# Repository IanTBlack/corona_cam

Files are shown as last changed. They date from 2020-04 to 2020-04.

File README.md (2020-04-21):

# Corona Cam
[The original In-situ Plankton Assemblage eXplorer (IPAX) was developed by Pichaya Lertvilai at UCSD](https://agu.confex.com/agu/osm20/meetingapp.cgi/Paper/648464). The Corona Cam is an attempt at recreating the IPAX that was presented at Ocean Sciences Meeting 2020.

Pichaya has set up a repo for the IPAX here: https://github.com/plertvilai/IPAX  

Similar to the IPAX, the Corona Cam seeks to provide a low cost method (~400 USD) for in-situ photography and video recording of very tiny things in the ocean (50-200 microns), such as zooplankton.

**Specs**

**Sensor Type: Sony IMX219 8MP**

**Lens: 1/2.5" 4mm M12 (swappable)**

**Brains: Raspberry Pi Zero W**

**LEDs: Adafruit NeoPixel Ring - 16x RGBW Cool White**

**Case: Blue Robotics 3" Watertight Enclosure (rated for 100m depth)**

**Battery: 5V rechargeable lithium-ion (i.e. cell phone power pack)**

**Video Resolution, Framerate, Format: 1920x1080, 30, .h264**

**Still Image Resolution: 3280x2464**  

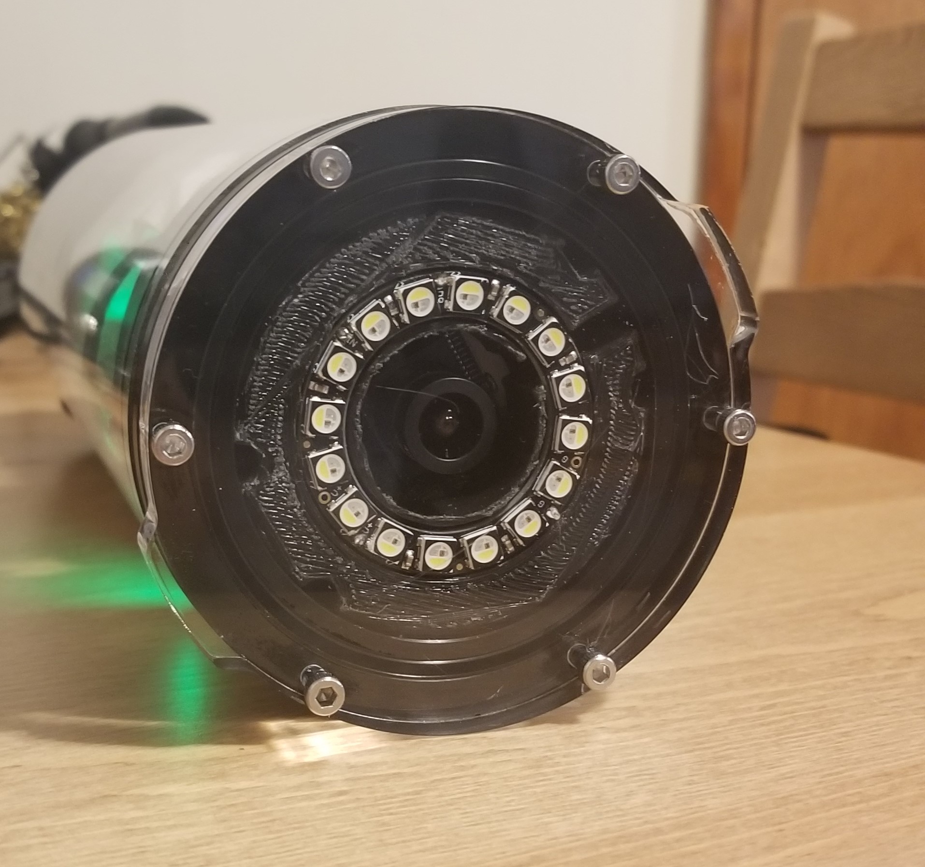
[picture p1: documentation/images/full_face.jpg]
Face


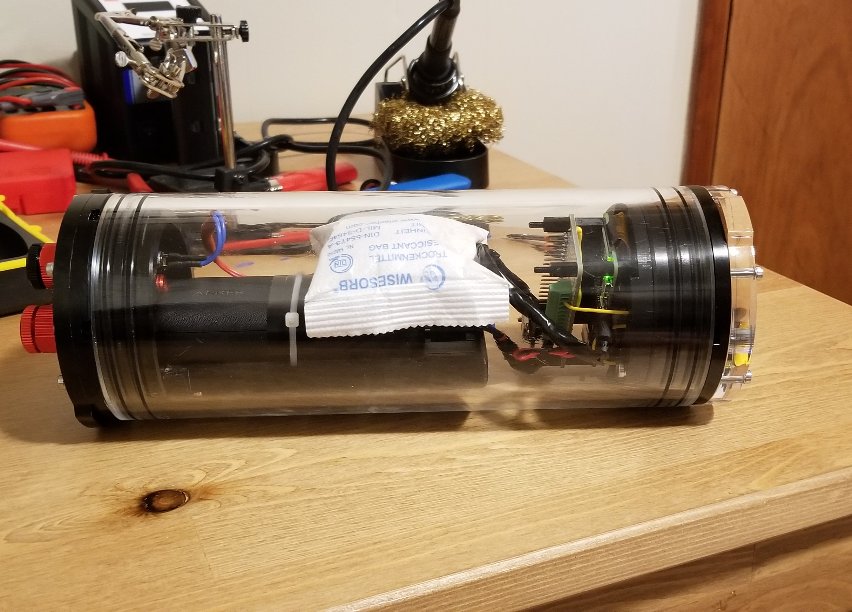
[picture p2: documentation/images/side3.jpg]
Side


The Corona Cam took approximately 9 pots of coffee and 72 Coronas to develop.

## Operation
The camera utilizes cron to operate at user-defined times. This allows the camera to operate at intervals or at specific times. The length of the recording, the recording format, and LEDs are controlled by the Python script that is run through cron.

## Repository Structure
### 3d_prints
This folder contains .ipt, .stl, and .gcode files for the camera mount, battery mount, and camera setup tool. For the .gcode files, Ultimaker Cura 4.5 was used as the slicer for printing on an Ender 5 Pro. The readme.txt file in that folder details the settings used. All three parts require approximately 300g of PLA and ~21 hours of print time.

### documentation
This folder contains drawings, guides, and manuals that were used in the development of the Corona Cam. It is recommended that you review this material if you run into any issues.
A build list is also provided. The primary vendors in this build list are Adafruit, Amazon, Blue Robotics, DLS Corp, and M12 Lenses. Note that the total price listed in the build list only considers the primary parts and does not consider 3D printing costs, consumables, tools, or other peripheral electronics (monitor, keyboard, mouse).

### scripts
This folder contains scripts for testing build components, a script that assists with setting up the Pi, and scripts that are run under crontab.

## Contact
For questions and comments, contact: Ian Black (blackia@oregonstate.edu)

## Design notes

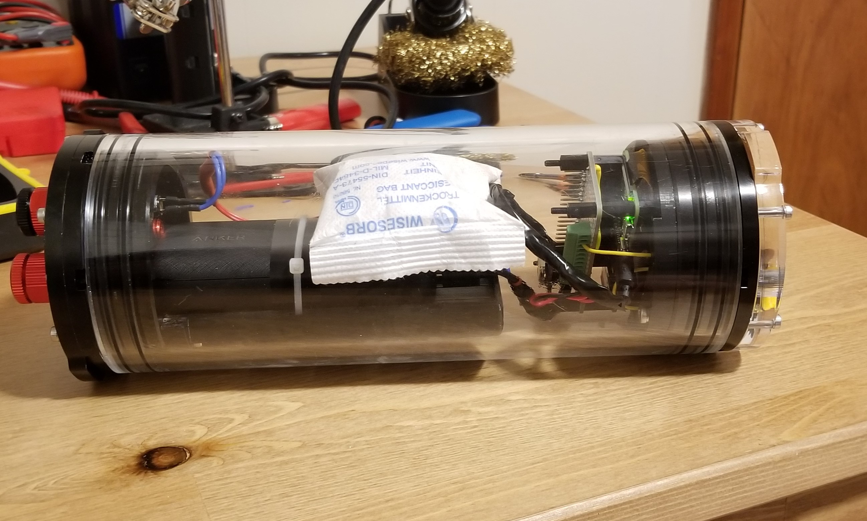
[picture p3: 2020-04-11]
documentation/images/side2.jpg

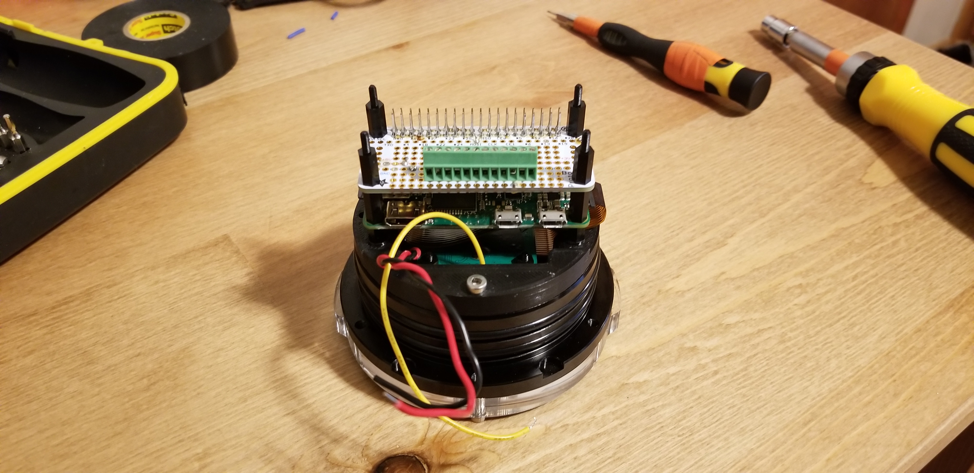
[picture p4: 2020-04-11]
documentation/images/cam_proto.jpg

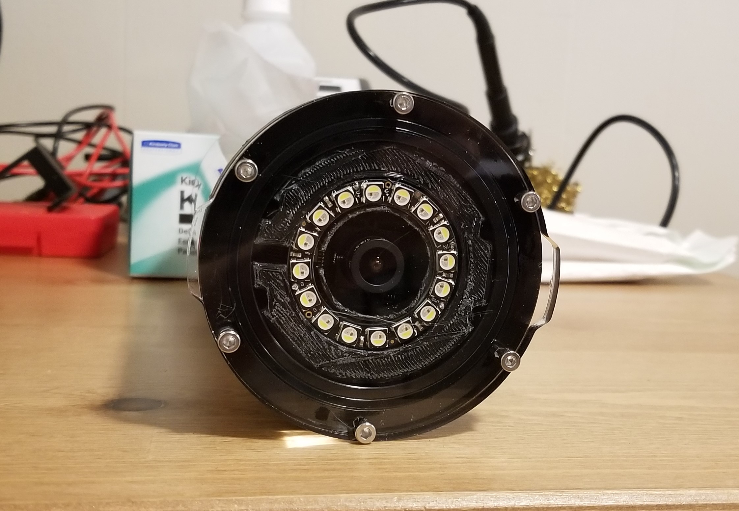
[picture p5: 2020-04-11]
documentation/images/cam_1.jpg

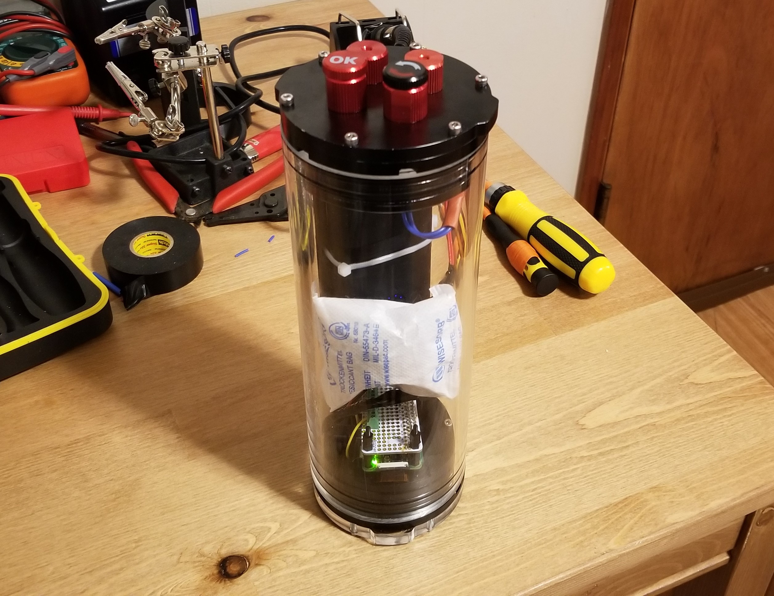
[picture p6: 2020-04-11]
documentation/images/tall.jpg

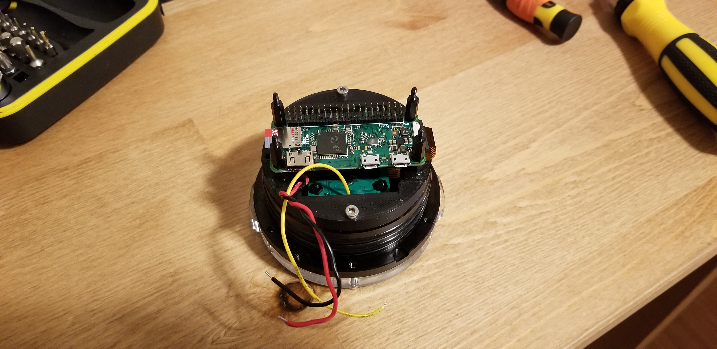
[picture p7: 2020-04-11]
documentation/images/pi_standoffs.jpg

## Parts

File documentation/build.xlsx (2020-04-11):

Total (Build) | 371.40
Part | Vendor | Part ID | Price Per Unit | Units | Subtotal | Comment | Check
Build
Raspberry Pi Zero W (https://www.adafruit.com/product/3400) | Adafruit | 3400 | 10.00 | 1 | 10.00 | Brains of the camera.
NeoPixel Ring - 16 RGBW (https://www.adafruit.com/product/2856) | Adafruit | 2856 | 11.95 | 1 | 11.95 | Lights for the camera.
Adafruit Perma Proto Bonnet Mini Kit (https://www.adafruit.com/product/3203) | Adafruit | 3203 | 4.50 | 1 | 4.50 | For connecting the NeoPixel/peripherals.
Raspberry Pi Zero v1.3 Camera Cable (https://www.adafruit.com/product/3157) | Adafruit | 3157 | 5.95 | 1 | 5.95 | For connecting the camera to the RPi.
Stacking Header for Pi - Extra Tall (https://www.adafruit.com/product/1979) | Adafruit | 1979 | 2.95 | 2 | 5.90 | For connecting the Protoboard to the Pi.
Adafruit PiRTC - DS3231 (https://www.adafruit.com/product/4282) | Adafruit | 4282 | 14.95 | 1 | 14.95 | For keeping time.
8-Pin Terminal Block (https://www.adafruit.com/product/2141) | Adafruit | 2141 | 2.75 | 1 | 2.75 | For connecting NeoPixel to protoboard.
Nylon Hex Standoffs - M2.5 (https://www.amazon.com/gp/product/B06XKWDSPT/ref=ppx_yo_dt_b_asin_title_o01_s00?ie=UTF8&psc=1) | Amazon | NLLZLM320PM25 | 12.99 | 1 | 12.99 | For connecting camera and RPi components to 3D printed camera mount.
CR1220 Coin Cell (https://www.amazon.com/Energizer-Lithium-Watch-Mercury-Batteries/dp/B00N9HRAAO) | Amazon | B00N9HRAAO | 5.49 | 1 | 5.49 | For powering PiRTC.
Breakaway Headers (https://www.adafruit.com/product/392) | Adafruit | 392 | 4.95 | 1 | 4.95 | Soldered to Pi.
3" Flange (https://bluerobotics.com/store/watertight-enclosures/3-series/o-ring-flange-3-series/) | Blue Robotics | WTE3-M-FLANGE-SEAL-R2-RP | 24.00 | 2 | 48.00 | Dual o-ring seal against the tube.
3" Aluminum End Cap - 4 Holes (https://bluerobotics.com/store/watertight-enclosures/3-series/wte3-m-end-cap-4-hole-r1/) | Blue Robotics | WTE3-M-END-CAP-4-HOLE-R1-RP | 12.00 | 1 | 12.00 | Single o-ring seal against the flange
3" Acrylic End Cap (https://bluerobotics.com/store/watertight-enclosures/3-series/wte3-p-end-cap-r1/) | Blue Robotics | WTE3-P-END-CAP-R1-RP | 10.00 | 1 | 10.00 | Single o-ring seal against the flange
3" Acrylic Tube - 8.75" (https://bluerobotics.com/store/watertight-enclosures/3-series/wte3-p-tube-8p75-r1/) | Blue Robotics | WTE3-P-TUBE-8P75-R1-RP | 35.00 | 1 | 35.00 | Main body of the camera.
Switch (https://bluerobotics.com/store/comm-control-power/switch/switch-10-5a-r1/) | Blue Robotics | SWITCH-10-5A-R1-RP | 15.00 | 1 | 15.00 | For turning the camera on and off.
Enclosure Vent Plug (https://bluerobotics.com/store/cables-connectors/penetrators/vent-asm-r1/) | Blue Robotics | VENT-ASM-R3-RP | 9.00 | 1 | 9.00 | For venting the camera.
M10 Blank Penetrator (https://bluerobotics.com/store/cables-connectors/penetrators/penetrator-blank-10-25-a-r2/) | Blue Robotics | PENETRATOR-M-BLANK-10-25-R3-RP | 4.00 | 2 | 8.00 | Placeholder for other sensors.
IMX219 - 8.0 MP Camera With M12 Mount (https://dlscorp.com/shop/imx219-8-0-mp-raspberry-pi-compatible-camera-module/) | DLS Corp | B0152 | 69.99 | 1 | 69.99 | Choose M12 Metal Mount - 16.5mm, No IR Filter
M12 1/2.5" 4mm Lens (http://www.m12lenses.com/4-0mm-F2-0-5MP-M12-Mount-CCTV-Lens-p/pt-0420cw-5mp.htm) | M12 Lenses | PT-0420CW-5MP | 17.00 | 1 | 17.00 | For taking video of tiny things.
microSD card - 128GB (https://www.amazon.com/Samsung-MicroSDXC-Adapter-MB-ME128GA-AM/dp/B06XWZWYVP) | Amazon | B06XWZWYVP | 21.99 | 1 | 21.99
Anker 10000mAh Power Pack (https://www.amazon.com/Anker-PowerCore-10000mAh-Portable-Delivery/dp/B07PXMF52C) | Amazon | B07PXMF52C | 33.99 | 1 | 33.99 | For powering the pi.
Right Angle microUSB Cable (https://www.amazon.com/s?k=microUSB+right+angle&ref=nb_sb_noss_2) | Amazon |  | 12.00 | 1 | 12.00 | Right angle allows for clearance to the case. An upward one might allow for connection to the PWR microUSB port, otherwise, use of the USB USB port is okay.
Consumables
Spare O-Rings (https://bluerobotics.com/store/watertight-enclosures/3-series/wte3-o-ring-set-r1/) | Blue Robotics | WTE3-O-RING-SET-R1-RP | 3.00 | 2 |  | You never know.
316SS M3 Hardware (Extra - 10mm long) | Blue Robotics | By Request |  |  |  | Extras for connecting 3D prints to flanges.
22 AWG Wire |  |  |  |  |  | Really just need three colors (V+,GND,signal).
AA Batteries (https://www.amazon.com/Energizer-Batteries-Battery-Alkaline-E91BP-24/dp/B004U429AQ) |  |  |  |  |  | For powering the camera.
Rosin Core Solder (https://www.amazon.com/Kester-solder-Rosin-Core-Spool/dp/B001W2XZOS) |  |  |  |  |  | For soldering wires.
Heatshrink
Tools
Penetrator Wrench (https://bluerobotics.com/store/cables-connectors/tools/tool-penetrator-wrench-r1/) | Blue Robotics | TOOL-PENETRATOR-WRENCH-R1-RP | 13.99 | 1 or 2 |  | Not necessary, but prevents marring of the aluminum during installation. Exposed aluminum will corrode when exposed to seawater for long periods of time.
Soldering Iron (https://www.amazon.com/gp/product/B00EO4CUHY/ref=ppx_yo_dt_b_search_asin_title?ie=UTF8&psc=1) |  |  |  |  |  | The XYTronic 258 will do what you need it to do. Nothing fancy.
Wire Strippers (https://www.amazon.com/Stripper-Stranded-Klein-Tools-11057/dp/B000XEUPMQ) |  |  |  |  |  | Just need to be able to strip 22 AWG.
Forceps |  |  |  |  |  | Helps when forming solder joints.
Flush Cutters |  |  |  |  |  | Helps when trimming pins and solder joints.
Third Hand
Electronics
Powered USB 2.0 Hub (https://www.amazon.com/gp/product/B07W3M16C1/ref=ppx_yo_dt_b_asin_title_o00_s00?ie=UTF8&psc=1) | Amazon | B07W3M16C1 | 17.99 | 1 |  | The Pi Zero can be tricky when hooking up peripherals. It only likes USB 2.0 and it can't really supply enough power for peripherals like a keyboard and mouse, so a separately powered USB 2.0 hub is required.
Mini-HDMI to HDMI (https://www.amazon.com/gp/product/B014I8UAPE/ref=ppx_yo_dt_b_asin_title_o02_s00?ie=UTF8&th=1) | Amazon | B014I8UAPE | 6.45 | 1 |  | RPi Zero to monitor.
Micro-USB to USB (https://www.amazon.com/gp/product/B00LN3LQKQ/ref=ppx_yo_dt_b_asin_title_o02_s00?ie=UTF8&psc=1) | Amazon | B00LN3LQKQ | 4.99 | 1 |  | Rpi Zero to powered USB 2.0 Hub to keyboard and mouse.
Monitor |  |  |  |  |  | Helps with initial set up , unless you are SSH savvy.
Keyboard
Mouse

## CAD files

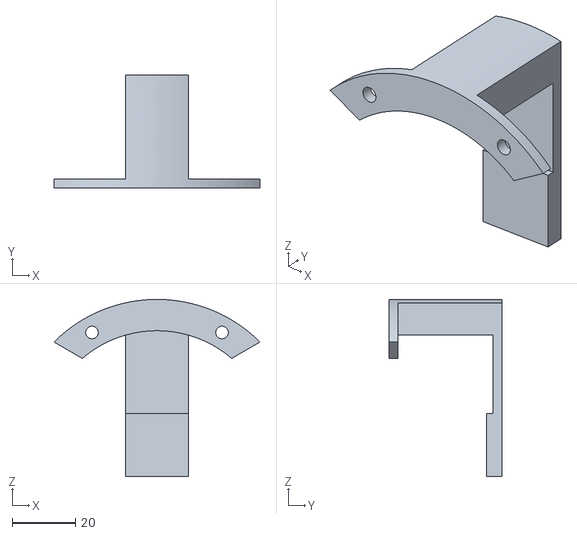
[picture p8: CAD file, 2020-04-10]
3d_prints/stl/corona_setup_tool.stl
65.4 x 36.0 x 56.2

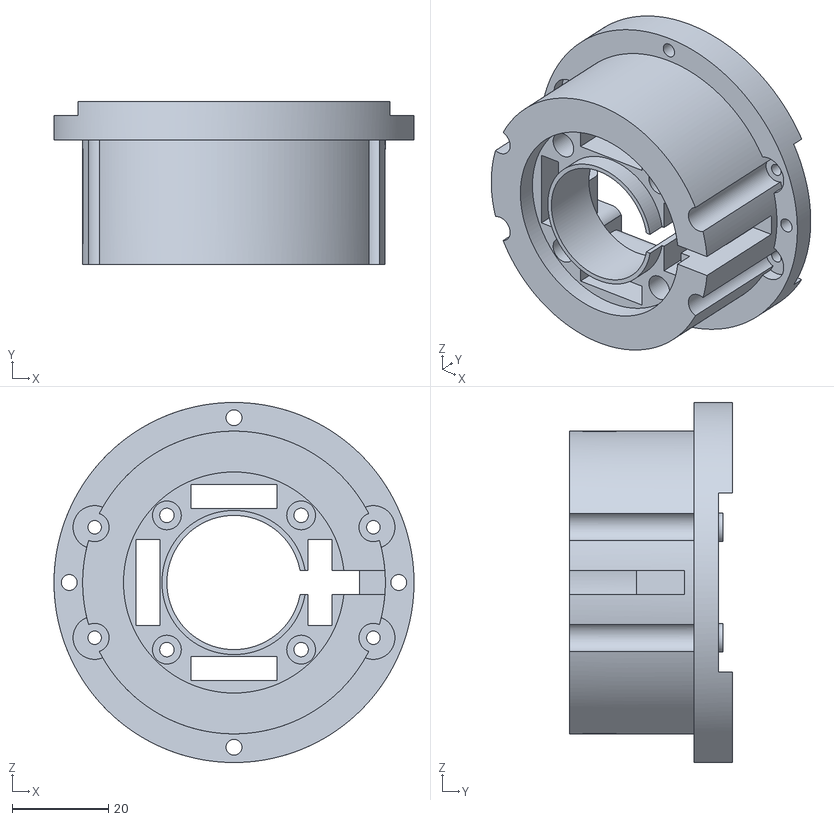
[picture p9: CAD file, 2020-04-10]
3d_prints/stl/corona_cam_mount.stl
74.9 x 34.0 x 74.9

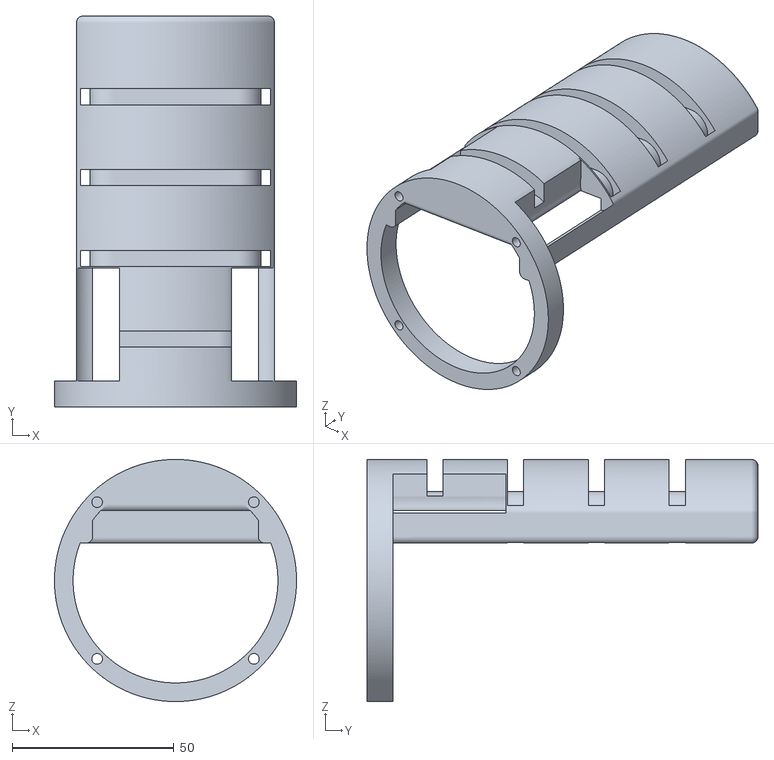
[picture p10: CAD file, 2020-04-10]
3d_prints/stl/corona_batt_mount.stl
74.9 x 121.0 x 74.9

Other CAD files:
3d_prints/ipt/corona_batt_mount.ipt
3d_prints/ipt/corona_cam_mount.ipt
3d_prints/ipt/corona_setup_tool.ipt

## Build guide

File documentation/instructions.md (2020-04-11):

# Instructions

## 1) Raspbian Install
I first recommend formatting your microSD card to FAT32. [The SD Association provides a simple application for formatting SD cards.](https://www.sdcard.org/downloads/formatter/)

There are a couple of ways you can flash Raspbian to your microSD card. The easiest method is to use [NOOBS](https://www.raspberrypi.org/downloads/noobs/), which walks you through setting up a Raspberry Pi through a graphical user interface (GUI). The second easiest method is to use the new [Raspberry Pi Imager](https://www.raspberrypi.org/downloads/), which provides a graphical user interface (GUI) for flashing Raspbian to your SD card, but does not set up things for you once installed.

Another method is to download the [Raspbian zip file](https://www.raspberrypi.org/downloads/raspbian/), unzip it with [7-zip (Windows)](https://www.7-zip.org/download.html) or [The Unarchiver(Mac)](https://theunarchiver.com/), and then flash the Raspbian img to your microSD card with an [imager that works with your system](https://www.raspberrypi.org/documentation/installation/installing-images/).  

Note: These instructions consider the use of the Raspbian GUI to facilitate easier setup and so that video recordings can be previewed when tuning the camera. When deploying the camera, I recommend having the Pi boot to the command line interface (CLI), this frees up memory and slightly reduces power consumption.

## 2) GitHub Repository Download
Instead of having to download files individually, you can download the whole GitHub repository using the git clone command.
Open terminal and ensure that you are in the default directory by entering the command:

```bash
cd /home/pi
```

Next, enter the command:

```bash
git clone https://github.com/IanTBlack/corona_cam.git
```

This will initiate a download of the entire repository. It may take a few minutes to download.

## 3) Changing Interface Settings
After you download the corona_cam repository, but before you run the setup script, you need to change a few interface settings on the Pi.

The Corona Cam requires the use of the camera, I2C, and serial port interfaces. If you are running the NeoPixel without sudo, you'll also need to activate the SPI interface.
You can change these settings by going to Applications Menu (raspberry icon on taskbar) > Preferences > Raspberry Pi Configuration. Once the configuration window opens, go to the Interfaces tab and enable camera, I2C, Serial Port, and Serial Console. Once you enable these, the RPi will ask to reboot.

Alternatively, you can open a terminal and enter the command: 'sudo raspi-config'. This provides a text-based interface for configuring the RPi.

## 4) Setting up the PiRTC (DS3231)
After you have soldered the breakaway headers to the RPi Zero W, attach the PiRTC with the coin cell installed. The directions outlined below are specific to the DS3231 PiRTC and also available in the [documentation/adafruit folder](https://github.com/IanTBlack/corona_cam/blob/master/documentation/adafruit/pi_rtc_adafruit_guide.pdf).

First, make sure the Pi is set to the timezone that you want. To make it simple, I usually set the locale to UK or the timezone to UTC.

Next, open a terminal session and enter:
```bash
sudo i2cdetect -y 1
```

You should see the number 68. This is the address of the PiRTC.

Next, we need to edit the boot configuration file. Issue the command:
```bash
sudo nano /boot/config.txt
```
Using the down arrow on the keyboard, scroll to the bottom of the file.
Type the following on a new line:
```bash
'dtoverlay=i2c-rtc,ds3231'
```
On the line below that one, type:
```bash
disable_camera_led=1
```
Type CTRL + O to write the changes. Then CTRL + X to exit the editor.
The first line we added above identifies the RTC as the DS3231.
The second line we added makes sure that the camera LED stays off.

To confirm your changes, type
```bash
sudo less /boot/config.txt
```

If everything looks good, restart the Pi with:

```bash
sudo reboot
```

Once the RPi is back up, we'll need to turn off the fake clock and tell the Pi to read from the PiRTC.

Issue the following:
```bash
sudo apt-get -y remove fake-hwclock
sudo update-rc.d -f fake-hwclock remove
sudo systemctl disable fake-hwclock
```

Once those commands have run their course, we'll need to edit another script.
Run:
```bash
sudo nano /lib/udev/hwclock-set
```
This will open a file for the original "hardware clock".
In this file, comment out the following lines with a '#' at the beginning of the line so that they look like this.

```bash
#if[-e /run/systemd/system]; then
# exit 0'
#fi
```

Scroll a little further down the file and also comment out these lines:

```bash
#/sbin/hwclock --rtc=$dev --systz --badyear
#/sbin/hwclock ==rtc=$dev --systz
```
Write out the script editor with CTRL + O and then exit with CTRL + X.

Next, check the clock time with
```bash
sudo hwclock -D -r
```
It should be wrong because we haven't set the time yet. Issue the following command to confirm that the time that be Pi states is correct.

```bash
date
```

To write the Pi time to the PiRTC, issue the command:
```bash
sudo hwclock -w
```

Then to check the PiRTC time:
```bash
sudo hwclock -r
```

The clock should now report the correct time.

## 5) Protoboard Setup and Testing
Next you can solder the tall headers and the terminal block to the protoboard.
We are using tall headers here because this allows the protoboard to stack on top of the Pi, and then the PiRTC on top of the protoboard.

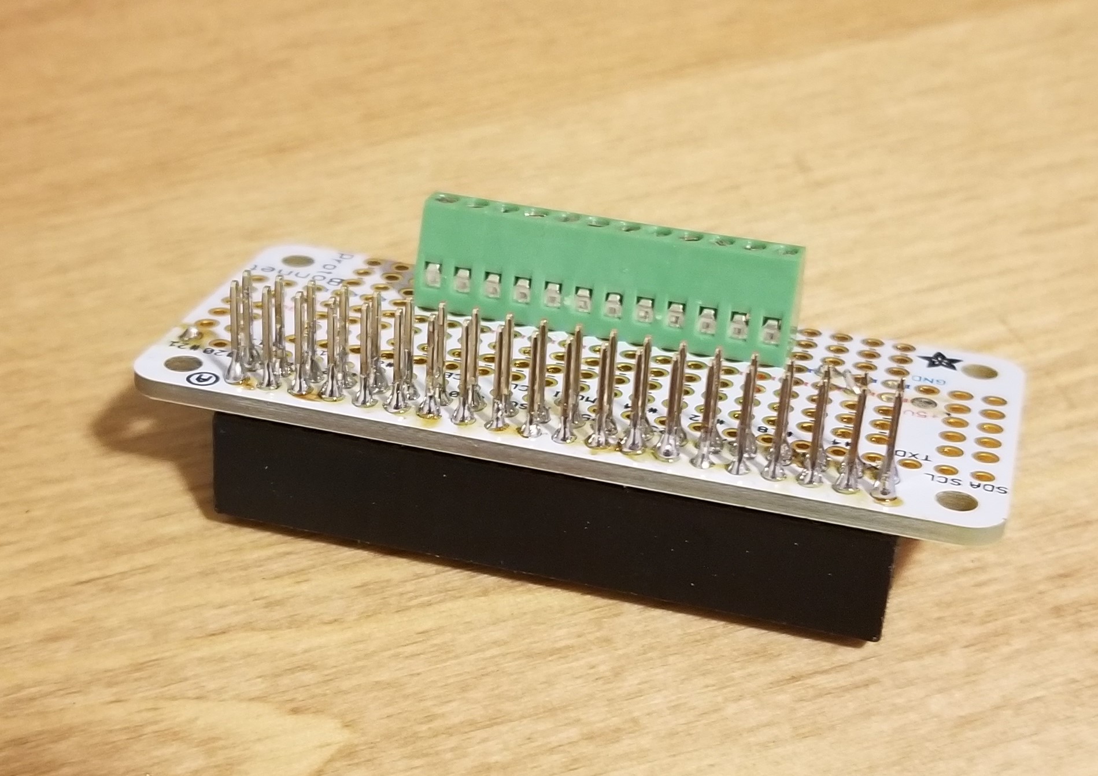
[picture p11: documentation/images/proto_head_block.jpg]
Headers

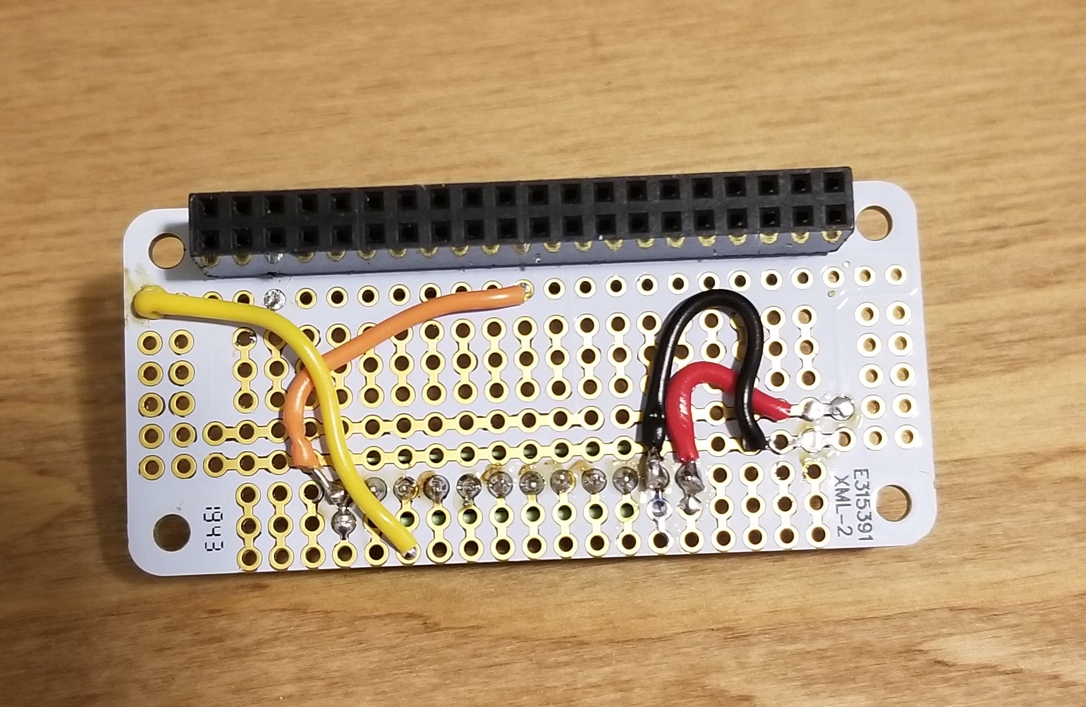
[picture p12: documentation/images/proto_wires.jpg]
Wires


In my version, I set up wires running from 5V, GND, Pin 21, and MOSI to pins on the terminal block. During testing, having the NeoPixel hooked up to MOSI allows you to not run the script as sudo, but can sometimes cause flickering. When deploying the camera, I have the NeoPixel hooked up the Pin 21.

## 6) NeoPixel Setup
Solder wires (~12cm long) to the V+, GND, and Input on the NeoPixel ring. Take care when doing this, as too much solder can short the ring, causing only some of the LEDs to light up.

## 7) Camera Side Setup
Install the 3D printed camera mount into the 3" Blue Robotics Flange using 10mm long, 3mm hex bolts. Then install 8mm M2.5 standoffs for the camera and 6mm M2.5 standoffs for the Pi. Note that M2.5mm hex standoffs can be tightened with a 5mm hex socket.
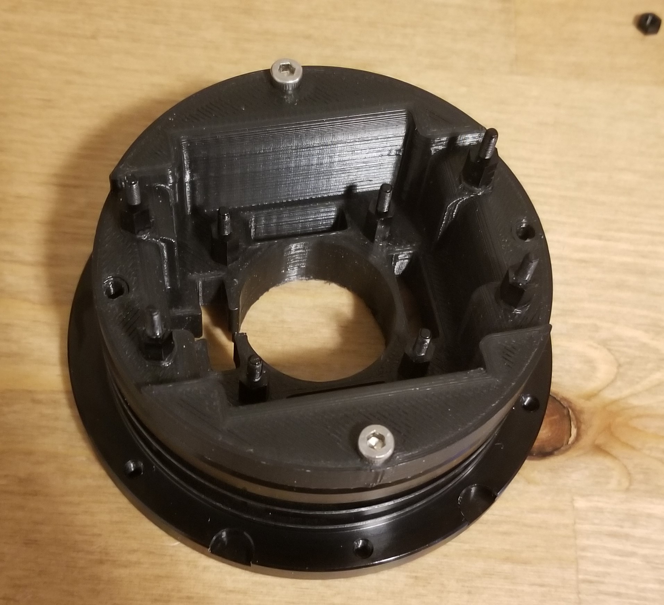
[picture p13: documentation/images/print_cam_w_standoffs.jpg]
Mount


Attach the camera cable to the camera. Install the camera into the 3D print. Use M2.5 nuts to secure the camera.
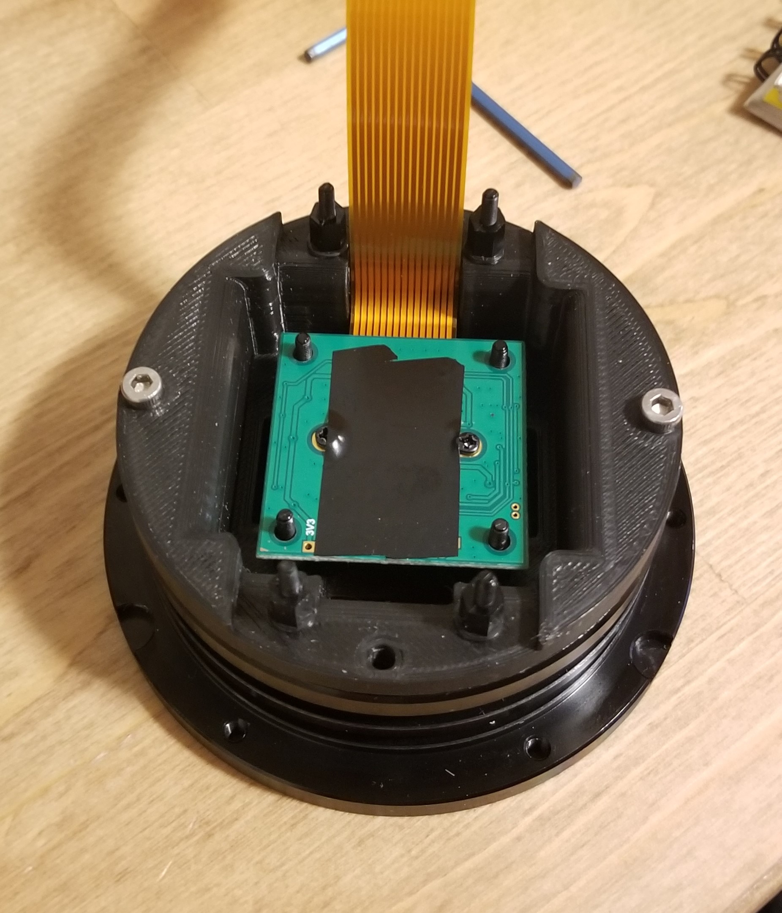
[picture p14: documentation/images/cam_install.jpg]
Cam_Install


Through the opposite side, thread the NeoPixel wires through the slots. The NeoPixel should sit freely within the grooves in the 3D print.

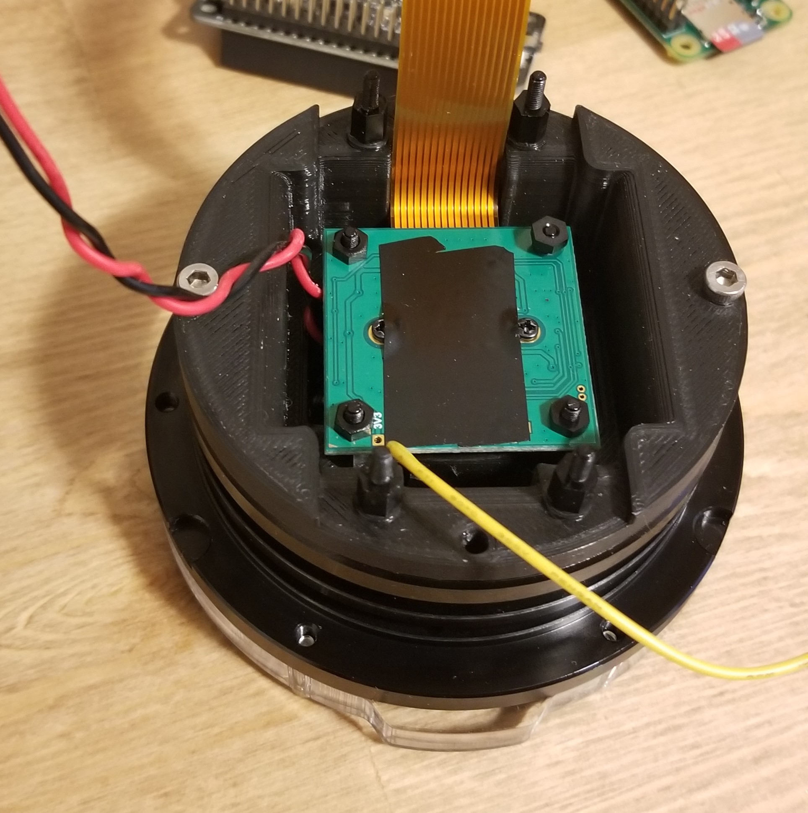
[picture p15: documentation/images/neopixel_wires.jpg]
NeoPixel Wires


Attach the camera cable to the Pi, and then install the Pi onto the 3D print. Secure the Pi in place with 12mm M2.5 standoffs.

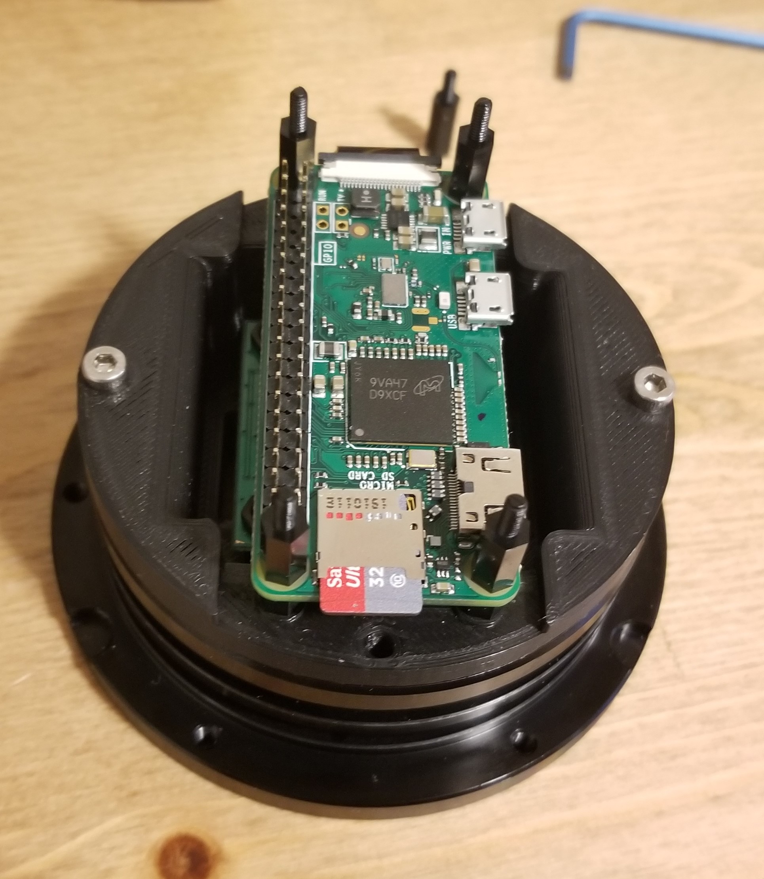
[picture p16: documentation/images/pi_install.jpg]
Pi_Standoffs


Install the protoboard setup on top of the Pi. Use 12mm M2.5 standoff to secure it in place.

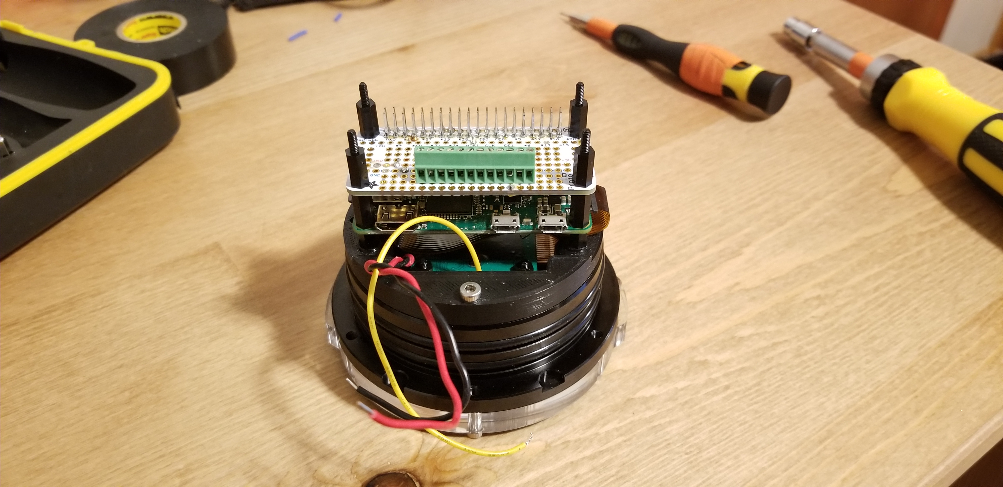
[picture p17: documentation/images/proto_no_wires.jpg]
Proto_Standoffs


Attach the Pi on top of the protoboard and secure with a M2.5 nut. Connect the NeoPixel wires to the appropriate terminal block locations.

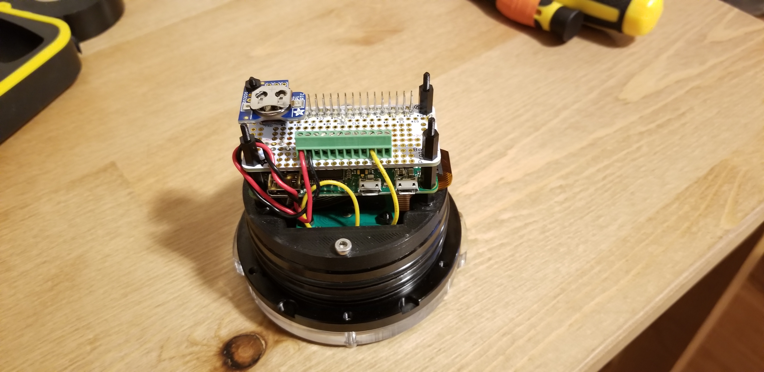
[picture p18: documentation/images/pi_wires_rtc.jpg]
RTC_Wires

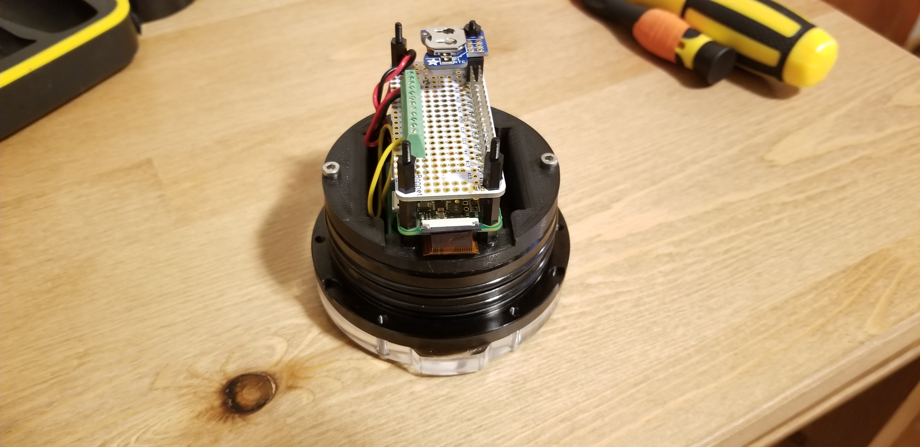
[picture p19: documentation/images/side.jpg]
Side

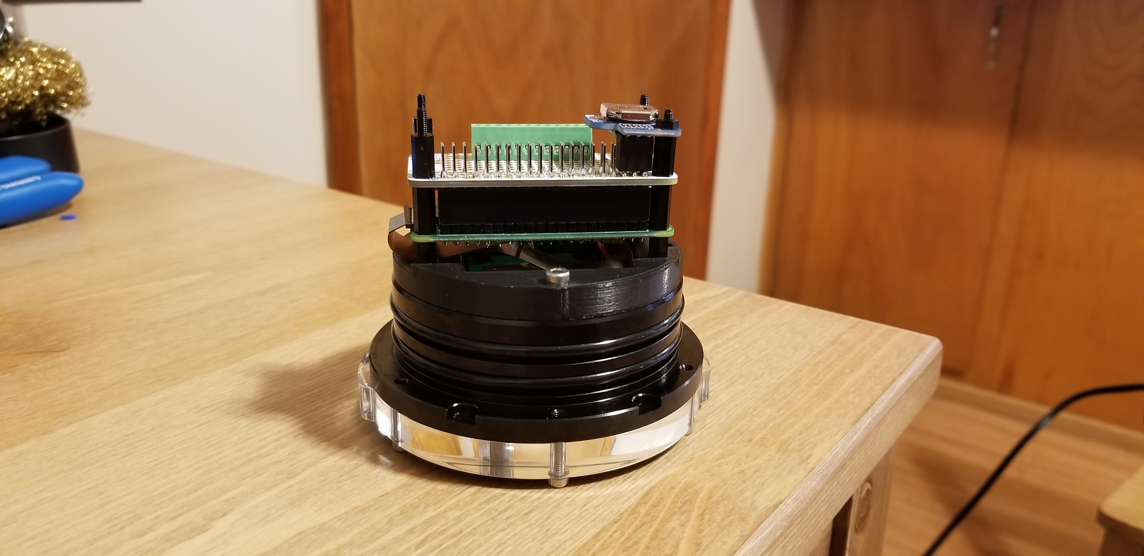
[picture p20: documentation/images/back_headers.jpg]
Back

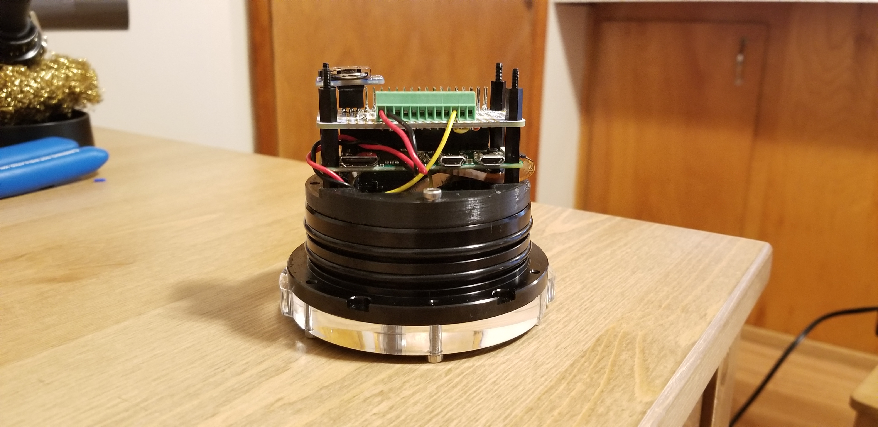
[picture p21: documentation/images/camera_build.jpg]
Build


## 8) Battery Side Setup
Install the Blue Robotics vent, switch, and blank plugs into the 4-hole end cap. Ensure that the o-rings are clean and greased.

Attach the 3D printed battery mount to the flange with two 10mm long M3 bolts. The switch should be oriented so that it is above the battery tray.

To make the switch cable, I found a microUSB cable that had enough clearance when plugged into the USB port on the PiZeroW. The PiZeroW USB port can also act as a power port for 5V sources. I took my cable and cut it in half. I then resoldered the GND sides back together, and for each V+ side, I soldered the switch wires that Blue Robotics provided with the switch. I would recommend purchasing a microUSB cable that has a 90 degree bend.

[The pinouts for USB hardware can be found on Wikipedia.](https://en.wikipedia.org/wiki/USB_hardware)
Since this cable will under go some strain when removing and attaching the battery pack, I recommend using the [Lineman's Splice](https://www.youtube.com/watch?v=O-ymw7d_nYo)

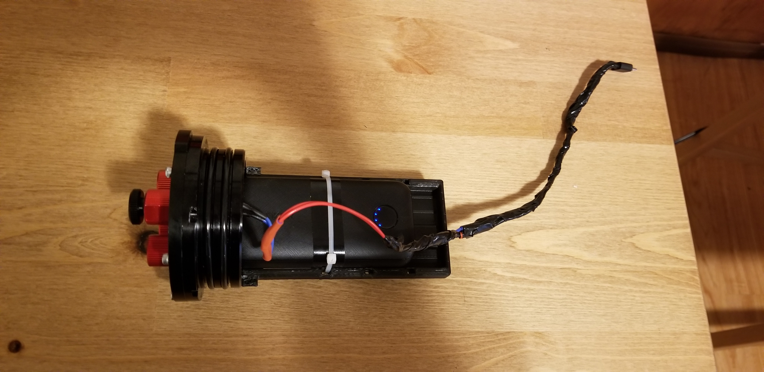
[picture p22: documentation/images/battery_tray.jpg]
Battery Side


## 9) Testing
After you have set up the NeoPixel, RTC, and camera you can test the build while it is attached to a monitor, keyboard, and mouse.
In terminal:
```bash
sudo python3 /home/pi/corona_cam/scripts/corona_cam.py
```

You should see that the LEDs turn blue for 30 seconds, then they turn white for 60 seconds. No preview should appear on the monitor (because it is currently disabled in the  Python script). To activate the preview in the corona_cam.py script, you will need to uncomment all lines that pertain to the camera preview in the run_camera function.

You can confirm that the camera produced a video by navigating to the h264 folder. The file should be titled 'corona_cam_YYYY-MM-DD_HHMM.h264'.

To test the camera, you can issue the command:

```bash
raspistill -t 60000
```
This will turn on the camera for 60 seconds and will display a preview on the monitor.
Utilizing this raspistill command is useful when tuning the camera.  Install the acrylic end cap over the camera along with the 3D printed setup tool. Adjust the camera lens until it is focused on the 3D print. The distance between the camera lens and the print is approximately 4cm. If the camera lens protrudes further than the end cap, you will need to break down the camera and adjust the length of the M2.5 standoffs that are used to hold the camera in place. Once focused, the viewing area of the camera is approximately 2cm x 2cm.

Once you are satisfied that the camera is operating correctly, you can set up a cron to run the corona_boot.sh script and the corona_cam.py script.

## 10) Crontab Setup
There are two scripts that need to be set up in Crontab in order for the camera to work. The corona_at_boot.sh script is a shell script that waits for 300s (5 minutes) after the Pi boots up before it turns off the HDMI port, WiFi, and ACT LED. During this five minutes, if you want to access the Pi, you can plug into it, comment out the boot script in Crontab and reboot the RPi..

The second script is the main operating code for the camera. You can set the frequency that the camera records via Cron. This can be done as an interval (i.e. every 60 minutes), or you can set it up to record at a specific time (i.e every hour at two minutes past the hour). Remember, this just modifies how often the camera records. If you want to change the length of time that the camera records, you'll need to change the record_time value in the Python script.

Note that each script will need its own line in crontab.

To access crontab, issue the following command in terminal:

```bash
crontab -e
```

If this is your first time setting up crontab, the easiest method is to use nano (method #1). At the bottom of the file, enter the following line:

```bash
 @reboot sudo sh /home/pi/corona_cam/scripts/corona_boot.sh
```

This will run the script every time the Pi reboots. Next we will want to run the operating Python script.
If you want to run the script every 15 minutes (independent of the clock time), enter the following on a new line:

```bash
*/15 * * * * sudo python3 /home/pi/corona_cam/scripts/corona_cam.py
```

If you want to run the script 15 minutes past the hour every hour, enter the following
```bash
15 * * * * sudo python3 /home/pi/corona_cam/scripts/corona_cam.py
````

This becomes particularly handy if you modify the corona_cam script and make copies that operate for different time lengths, take pictures, have different camera resolutions, different LED colors, etc. You could have two different scripts run at different times. [Crontab Guru](https://crontab.guru/#*_*_*_*_*) is a handy tool for determining crontab scheduling.

Once you have set up the lines in crontab file, write out the changes with CTRL + O, and then exit with CTRL + X.

To check if your changes were made, issue the command:

```bash
crontab -l
```

## 11) Final Seal
Things to consider before deployment.
- Is the battery charged and zip-tied in place?
- Do any of the acrylic pieces have scratches that would cause flooding?
- Are all of the o-rings in place and greased (especially the end caps, vent, and switch)?
- Did I add a desiccant pack?
- Is there enough space on the SD card?
- Did I set up the crontab correctly?
- Did I apply a vacuum to the unit?

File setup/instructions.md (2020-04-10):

# Order of Operations
## Raspbian Install
I first recommend formatting your microSD card to FAT32.
[The SD Association provides a simple application for formatting SD cards.](https://www.sdcard.org/downloads/formatter/)

While your microSD card is formatting, you can download the [Raspbian Imager](https://www.raspberrypi.org/documentation/installation/installing-images/README.md), which allows you to flash Raspbian to the card. It is not recommended that you install Raspbian with NOOBS. If you decided to implement the Zero2Go Omini, NOOBS can cause problems with its operation.

Once your card has Raspbian loaded onto it, pop it into the RPiZeroW and fire up the system.

Note: These instructions initially consider use of the Raspbian GUI (mostly because I am a visual learner). When deploying the camera, I recommend having the Pi boot to the command line interface (CLI), this frees up memory and slightly reduces power consumption.

## GitHub Repository Download
Instead of having to download files individually, you can download the whole GitHub repository using the git clone command.
Open terminal and ensure that you are in the default directory (/home/pi).

Next, enter the command:

> git clone https://github.com/IanTBlack/corona_cam.git

This will initiate a download of the entire repository.

## Run Setup Script
I've created a shell script that will install the necessary python libraries and third party software for operating the camera.
This makes it so you don't have to set up everything yourself. Although if you still want to do that, you can look at the scripts.
In terminal, execute the following commands:

> cd /home/pi/corona_cam/setup
> chmod +x corona_setup.sh
> cd /home/pi/
> sudo sh /home/pi/corona_cam/setup/corona_setup.sh

This will install some libraries and setup a new directory in the corona_cam folder for recorded videos. It will also set up corona_boot.sh and corona_cam.py to be executable.

## Zero2Go Omini Setup and Testing
Once the corona_setup.sh script runs and the Pi reboots, you can set up the Zero2Go Omini. The setup script should take care of installation.

Once you physically mount the pHat, you can configure the Zero2Go.
Enter the following commands in terminal:

> cd zero2go
> ./zero2go.sh

A console will appear in the terminal that lets you configure the Zero2Go defaults.

You'll want to change the default state when power is connected to ON.
Set the blinking interval to 8 seconds.
If you want to camera to safely shutdown at a low voltage, you can configure it based on the battery voltage.

## Protoboard Setup and Testing

## RTC Setup and Testing

## Boot Script Setup

## Operating Script Setup

## Crontab Setup
There are two scripts that need to be set up in Crontab in order for the camera to work. The corona_at_boot.sh script is a shell script that waits for 600s (10 minutes) after the Pi boots up before it turns off the HDMI port, WiFi, and ACT LED. During this ten minutes, if you want to access the Pi, you can plug into it, comment out the boot script in Crontab, and the reboot it.

The second script is the main operating code for the camera. You can set the frequency that the camera records. This can be done as an interval (i.e. every 60 minutes), or you can set it up to record at a specific time (i.e every hour at two minutes past the hour). Remember, this just modifies how often the camera records. If you want to change the length of time that the camera records, you'll need to change the record_time value in the Python script.

If you kept the defaults, here is how you would set up the boot script via terminal.

> cd /corona_cam/scripts
> chmod +x corona_at_boot.sh
> cd /home/pi
> crontab -e

If this is your first time setting up crontab, the easiest method is to use method 1 (nano). At the bottom of the file, enter the following line:

> @reboot /home/pi/corona_cam/scripts/corona_at_boot.sh

Next, you'll want to add the operating script.

> cd /home/pi/corona_cam/scripts
> chmod +x corona_cam.py
> cd /home/pi
> crontab -e

If you want to run the script every 60 minutes (independent of the clock time), enter the following:

> */60 * * * * sudo python3 /home/pi/corona_cam/scripts/corona_cam.py

If you want to run the script 5 minutes past the hour every hour, enter the following
5 * * * * sudo python3 /home/pi/corona_cam/scripts/corona_cam.py

[Crontab Guru](https://crontab.guru/#*_*_*_*_*) is a handy tool for determining crontab scheduling.

Following these instructions in order is recommended.

1) Install SD Formatter  and format your SD card.

1) Flash Raspbian to your SD card. The easiest method is with the Raspbian Imager (https://www.raspberrypi.org/documentation/installation/installing-images/README.md)
   DO NOT INSTALL WITH NOOBS. Installing with NOOBS can cause problems with the Zero2Go Omini.

1) Run corona_setup.sh
	a) cd Corona_Cam
	b) chmod +x corona_setup.sh
	c) ./corona_setup.sh
	d) Once complete, the Pi will reboot.

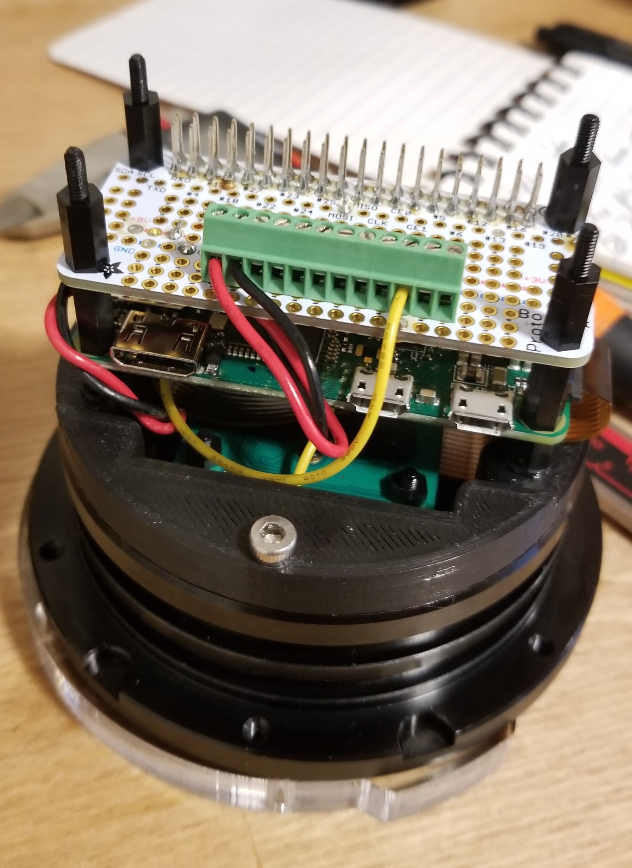
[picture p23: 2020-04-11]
documentation/images/proto_install.jpg

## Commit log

2020-04-10 Found potential issue with installing Zero2Go software.
    [build.xlsx]
2020-04-10 Removed references to the Zero2Go Omini.
    It it too frustrating to use.
    [build.xlsx]
2020-04-11 Updated build list.
    [build.xlsx]
2020-04-11 Updated build.xlsx
    [build.xlsx]
